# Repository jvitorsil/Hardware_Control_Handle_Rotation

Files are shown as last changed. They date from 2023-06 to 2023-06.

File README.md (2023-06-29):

# Hardware_Control_Handle_Rotation

Sistema embarcado para controle de rotação de punho em próteses bioelétricas através de sensores inerciais.

O sistema conta com a utilização de dois acelerometro acoplados ao paciente, acoplados respectivamente em paralelo na região antero-lateral do torax nos musculos intercostais e outro localizado no triceps braquial. O funcionamento está baseado na agulação criada entre os sensores pelo movimento de abdução do braço, gerando assim um movimento de pronação e supinação da protese.

O circuito eletronico conta com a utilização de um micrcontrolador STM32F103C8T6, com toda parte de Debug, reset e clock adicionada ao circuito. 

As proteses mioeletricas atuais contam na maioria das vezes com motores DC e para o acionamento do mesmo foi utilizado do driver L293D, que consegue controlar a velocidade e sentido de rotação do motor através da modulação dos pulsos de PWM gerado.

Já para a parte de entrada de dados foi definido o sensor MPU6050, contando com protocolo de comunicação I2C.

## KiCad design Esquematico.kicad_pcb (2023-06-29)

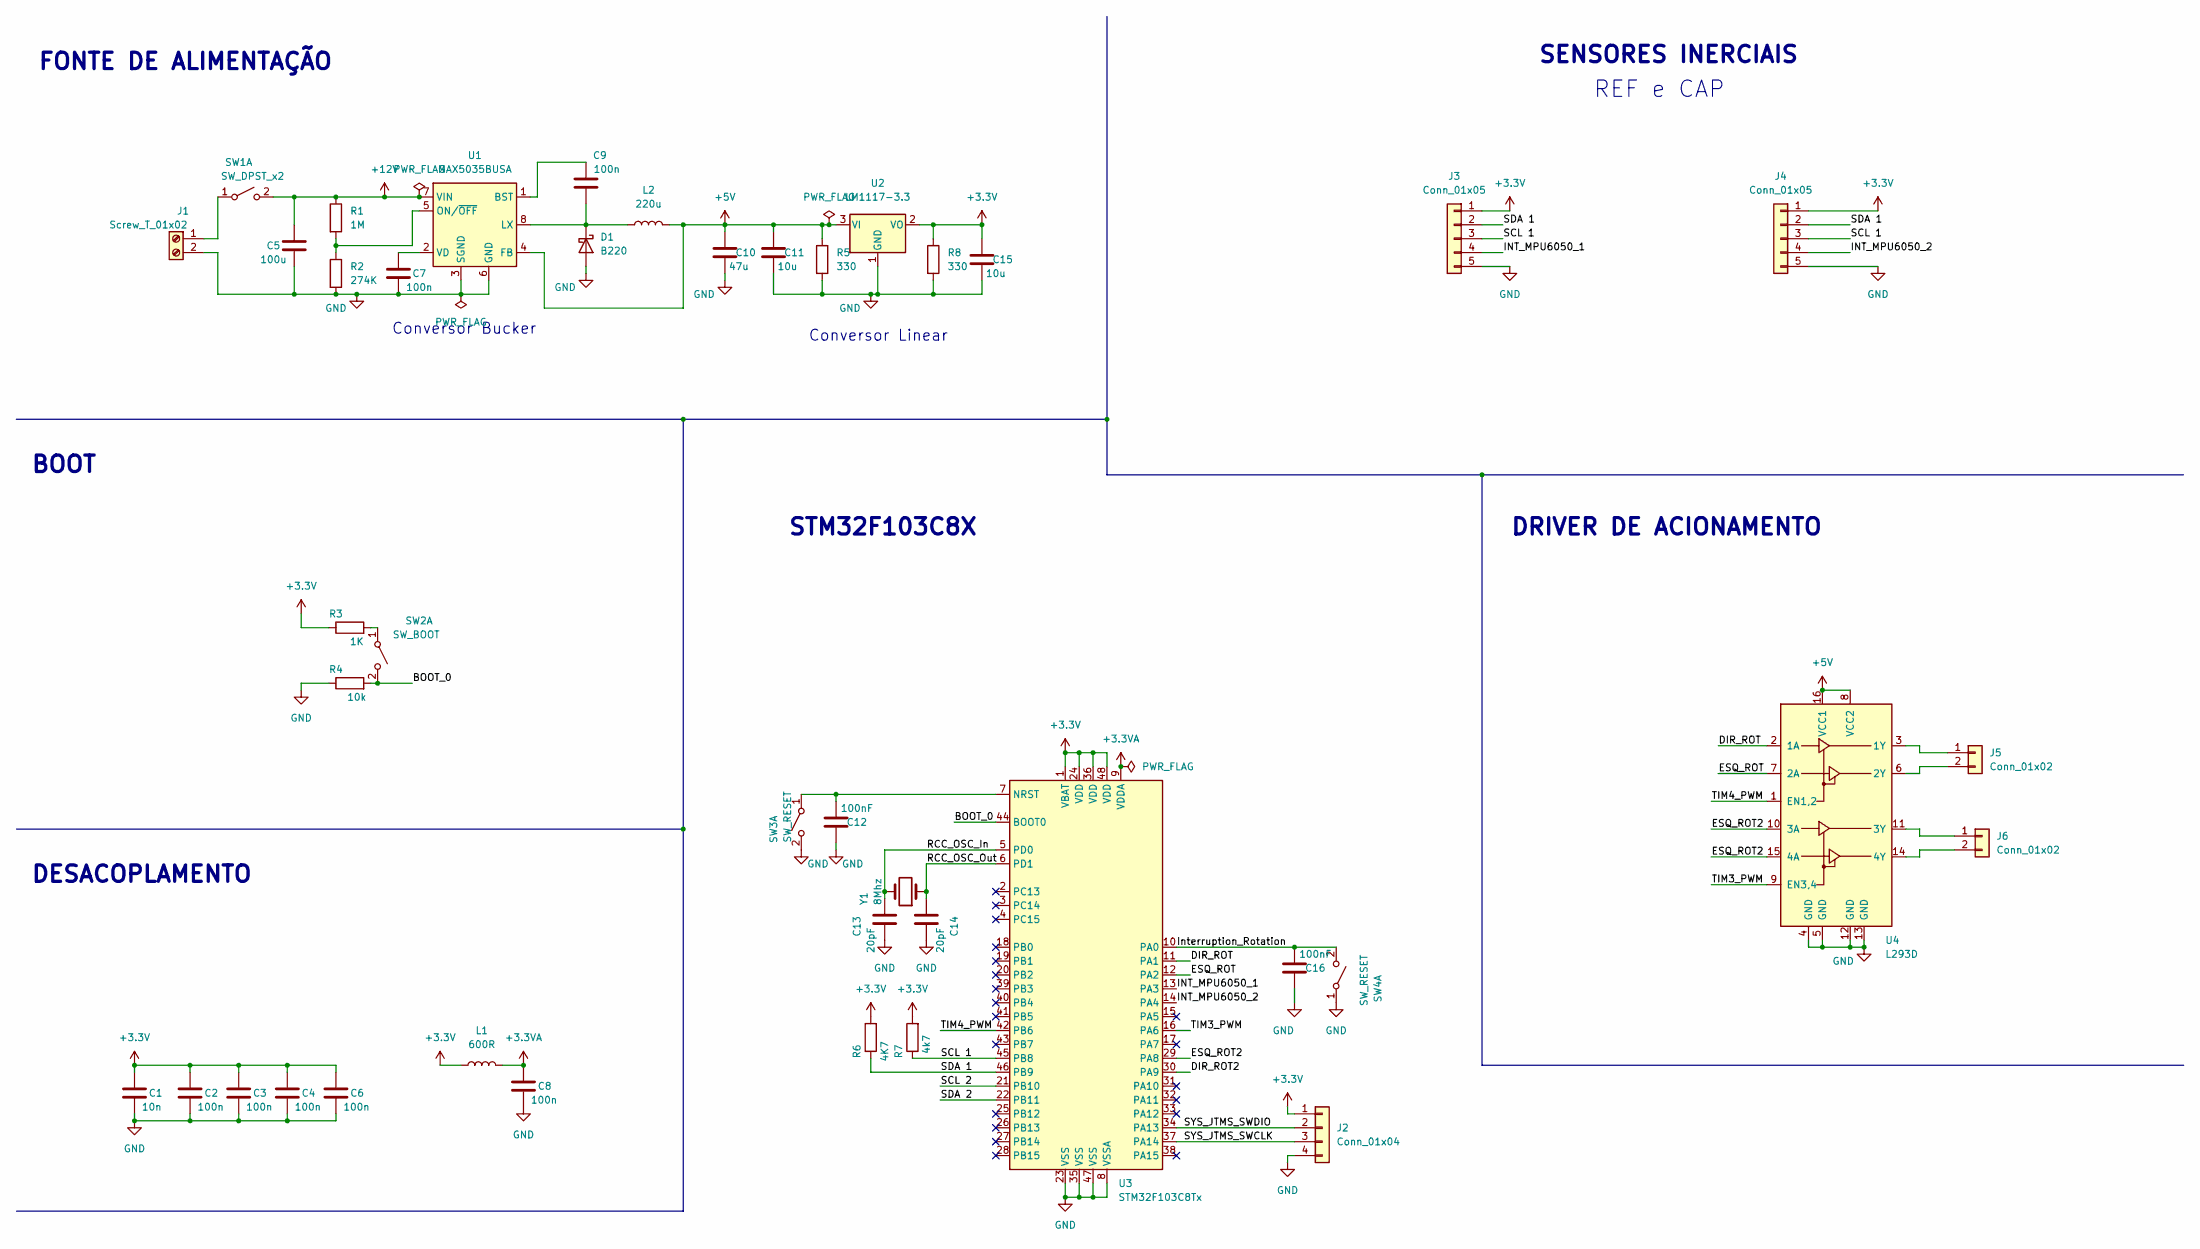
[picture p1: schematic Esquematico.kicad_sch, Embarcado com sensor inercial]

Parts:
C1: 10n; C_0402_1005Metric
C2, C3, C4, C6, C8: 100n; C_0402_1005Metric
C5: 100u; C_0805_2012Metric
C7, C9: 100n; C_0805_2012Metric
C10: 47u; C_0805_2012Metric
C11, C15: 10u; C_0805_2012Metric
C12, C16: 100nF; C_0402_1005Metric
C13, C14: 20pF; C_0603_1608Metric
D1: B220; D_SMF
J1: Screw_T_01x02; JST_PH_S2B-PH-SM4-TB_1x02-1MP_P2.00mm_Horizontal
J2: Conn_01x04; JST_PH_S4B-PH-SM4-TB_1x04-1MP_P2.00mm_Horizontal
J3, J4: Conn_01x05; JST_PH_S5B-PH-SM4-TB_1x05-1MP_P2.00mm_Horizontal
J5, J6: Conn_01x02; JST_PH_S2B-PH-SM4-TB_1x02-1MP_P2.00mm_Horizontal
L1: 600R; L_0603_1608Metric
L2: 220u; L_0603_1608Metric
R1: 1M; R_0805_2012Metric
R2: 274K; R_0805_2012Metric
R3: 1K; R_0805_2012Metric
R4: 10k; R_0805_2012Metric
R5, R8: 330; R_0805_2012Metric
R6: 4K7; R_0805_2012Metric
R7: 4k7; R_0805_2012Metric
SW1: SW_DPST_x2; SW_DIP_SPSTx01_Slide_6.7x4.1mm_W6.73mm_P2.54mm_LowProfile_J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
SW2: SW_BOOT; SW_SPST_B3U-1000P-B
SW3, SW4: SW_RESET; SW_SPST_B3U-1000P-B
U1: MAX5035BUSA; SOIC-8_3.9x4.9mm_P1.27mm
U2: LM1117-3.3; SOT-223-3_TabPin2
U3: STM32F103C8Tx; LQFP-48_7x7mm_P0.5mm
U4: L293D; DIP-16_W7.62mm
Y1: 8Mhz; Crystal_SMD_HC49-SD

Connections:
+3.3V: C1.1, C2.1, C3.1, C4.1, C6.1, C15.2, J2.1, J3.1, J4.1, L1.1, R3.1, R6.2, R7.2, R8.1, U2.2 (VO), U3.1 (VBAT), U3.24 (VDD), U3.36 (VDD), U3.48 (VDD)
+3.3VA: C8.1, L1.2, U3.9 (VDDA)
+5V: C10.2, C11.2, L2.2, R5.1, U1.4 (FB), U2.3 (VI), U4.8 (VCC2), U4.16 (VCC1)
+12V: C5.2, R1.1, SW1.2 (B), U1.7 (VIN)
/BOOT_0: R4.2, SW2.2 (B), U3.44 (BOOT0)
/DIR_ROT: U3.11 (PA1), U4.2 (1A)
/DIR_ROT2: U3.30 (PA9)
/ESQ_ROT: U3.12 (PA2), U4.7 (2A)
/ESQ_ROT2: U3.29 (PA8), U4.10 (3A), U4.15 (4A)
/INT_MPU6050_1: J3.4, U3.13 (PA3)
/INT_MPU6050_2: J4.4, U3.14 (PA4)
/Interruption_Rotation: C16.1, SW4.2 (B), U3.10 (PA0)
/RCC_OSC_In: C13.2, U3.5 (PD0), Y1.2
/RCC_OSC_Out: C14.2, U3.6 (PD1), Y1.1
/SCL 1: J3.3, J4.3, R7.1, U3.45 (PB8)
/SCL 2: U3.21 (PB10)
/SDA 1: J3.2, J4.2, R6.1, U3.46 (PB9)
/SDA 2: U3.22 (PB11)
/SYS_JTMS_SWCLK: J2.3, U3.37 (PA14)
/SYS_JTMS_SWDIO: J2.2, U3.34 (PA13)
/TIM3_PWM: U3.16 (PA6), U4.9 (EN3,4)
/TIM4_PWM: U3.42 (PB6), U4.1 (EN1,2)
GND: C1.2, C2.2, C3.2, C4.2, C5.1, C6.2, C7.1, C8.2, C10.1, C11.1, C12.2, C13.1, C14.1, C15.1, C16.2, D1.2 (A), J1.2, J2.4, J3.5, J4.5, R2.2, R4.1, R5.2, R8.2, SW3.2 (B), SW4.1 (A), U1.3 (SGND), U1.6 (GND), U2.1 (GND), U3.8 (VSSA), U3.23 (VSS), U3.35 (VSS), U3.47 (VSS), U4.4 (GND), U4.5 (GND), U4.12 (GND), U4.13 (GND)
unnamed: C7.2, U1.2 (VD)
unnamed: C9.1, D1.1 (K), L2.1, U1.8 (LX)
unnamed: C9.2, U1.1 (BST)
unnamed: C12.1, SW3.1 (A), U3.7 (NRST)
unnamed: J1.1, SW1.1 (A)
unnamed: J5.1, U4.3 (1Y)
unnamed: J5.2, U4.6 (2Y)
unnamed: J6.1, U4.11 (3Y)
unnamed: J6.2, U4.14 (4Y)
unnamed: R1.2, R2.1, U1.5 (ON/~OFF)
unnamed: R3.2, SW2.1 (A)

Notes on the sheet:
SENSORES INERCIAIS
REF e CAP
BOOT
DESACOPLAMENTO
STM32F103C8X
Conversor Bucker
FONTE DE ALIMENTAÇÃO
DRIVER DE ACIONAMENTO
Conversor Linear

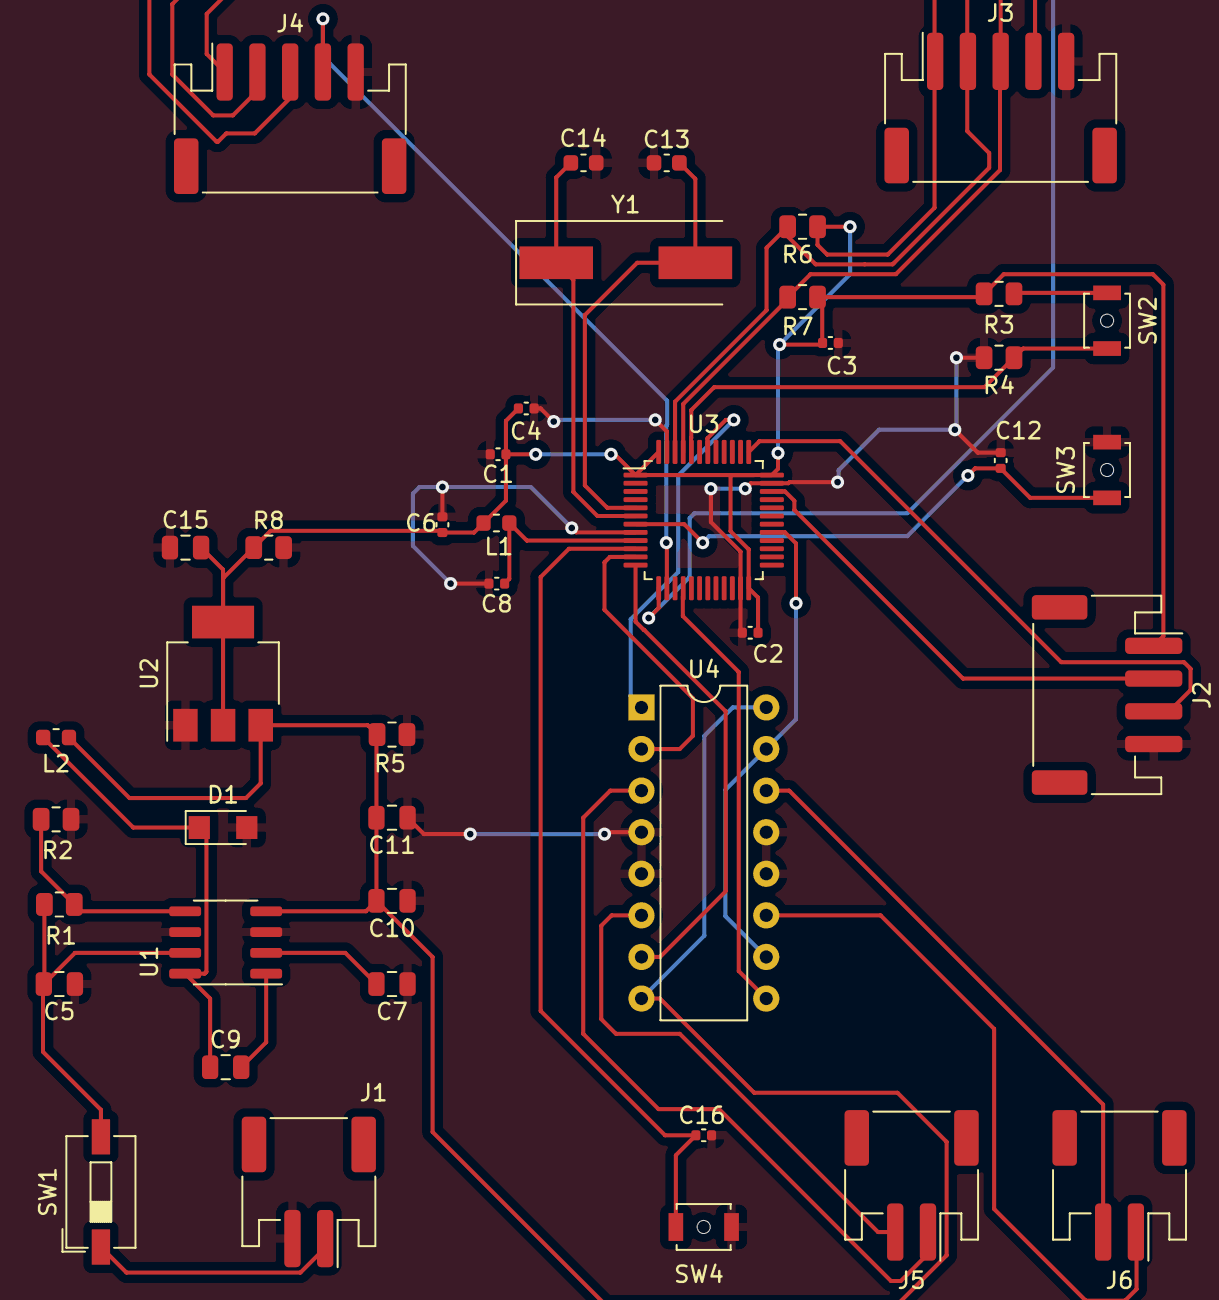
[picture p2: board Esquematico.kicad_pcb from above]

Board: 2 copper layers, 42 parts (0 on the bottom side), 31 nets.
